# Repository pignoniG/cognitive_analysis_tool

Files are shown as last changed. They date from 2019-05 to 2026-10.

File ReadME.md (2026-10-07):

# Cognitive Workload Tool 2.0

Luminance-compensated pupillometry: an estimate of cognitive workload from the pupil that can be used outside the
laboratory's constant lighting.

The pupil dilates with cognitive workload but reacts far more strongly to light. The tool estimates the pupil size
the light reaching the eye should produce (Watson & Yellott's unified formula, with the participant's latency and
pupil dynamics), and reports what is left, the **ΔPD**:

```
ΔPD(t) = measured pupil(t) − expected pupil(luminance(t))
```

The luminance is estimated from the eye tracker's scene video and gaze: a circle around the gaze point weighted
against the rest of the view. On a headset it comes from the display's photometry; with glasses trackers, the
absolute level comes from a lux sensor worn on the tracker.

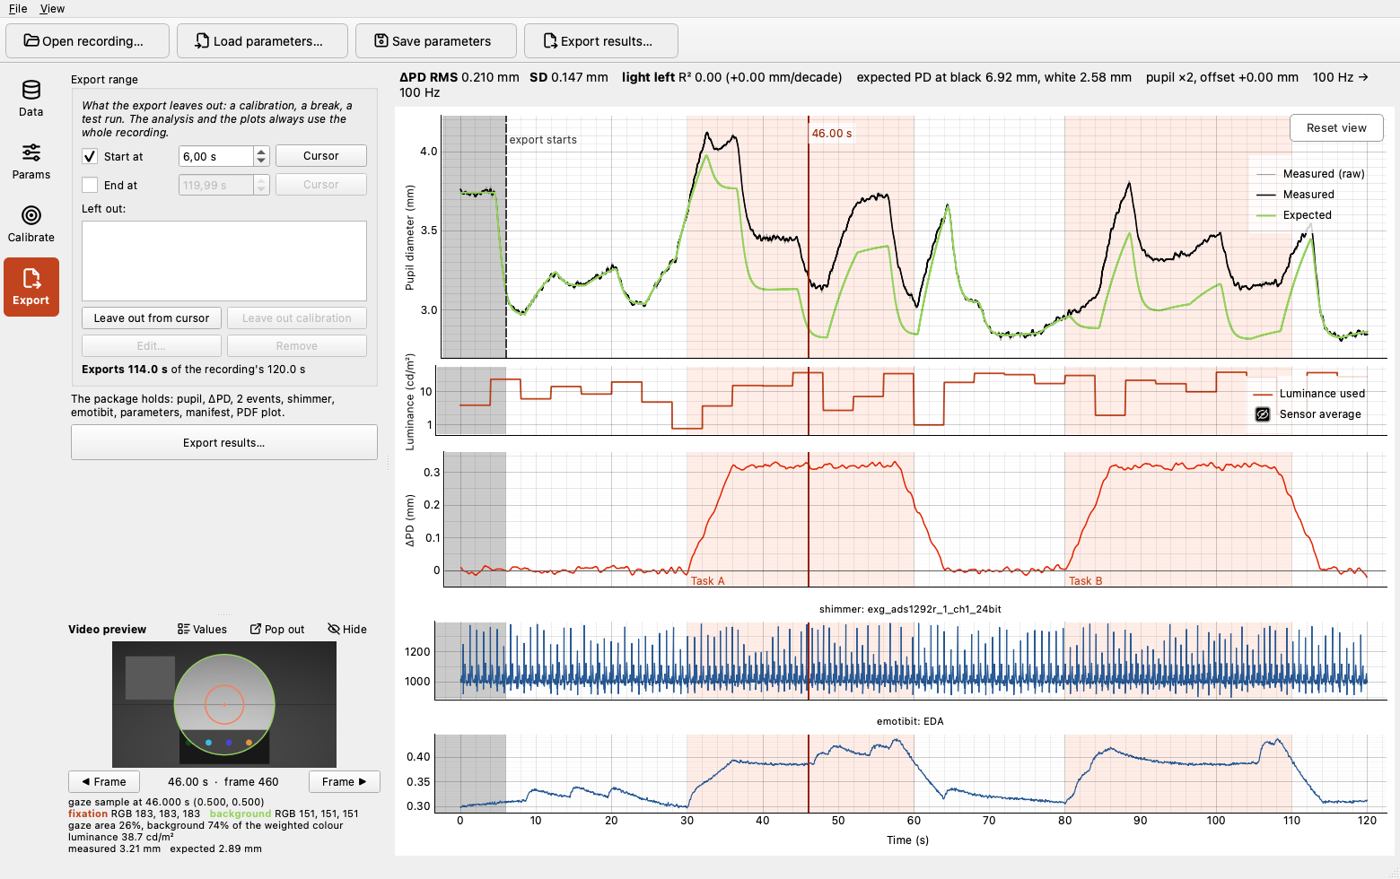
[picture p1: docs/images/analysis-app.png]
The analysis app on a synthetic recording: measured and expected pupil, luminance, ΔPD with two task phases, and the ECG and EDA from the sensor logger


*The analysis app on synthetic data: a task that dilates the pupil twice, the light that changes every few seconds, and the ΔPD that is left once the light is accounted for, with the Shimmer's ECG and the EmotiBit's EDA on the same time axis.*

**Documentation:** https://pignonig.github.io/cognitive_analysis_tool/ covers installation, usage, the device
formats and every processing step ([Processing at a glance](https://pignonig.github.io/cognitive_analysis_tool/processing/pipeline/)).
Its source is in `docs/`.

> Version 2.0 is in development. The 1.x tools are kept, for archive only, on the `legacy-*` branches.

## Supported devices

| Device | Recording | Luminance from | Support |
|---|---|---|---|
| Varjo XR-4 | Varjo Base eye tracking recorder | the display: scene capture, display photometry, participant light sensitivity | tested |
| Pupil Core | Pupil Player export | external lux sensor + scene video | tested |
| Pupil Neon | Pupil Cloud Timeseries export or native format | external lux sensor + scene video | experimental |
| Tobii Pro Glasses 3 | recording folder from the SD card | external lux sensor + scene video | experimental |

Experimental readers were written from the manufacturer's documentation and have not yet been checked on a real
recording; every result from them carries a warning.

## The tools

**Analysis app** (`cwtool-gui`). Open a recording folder: the scene video is analysed in the background (or loaded
from its cache), and every parameter change updates the measured and expected pupil and ΔPD plots at once. A video
preview shows the analysed areas on the scene frame at the cursor. Sensor files from the logger can be shown under
ΔPD. **Export** writes one package for the participant: pupil, ΔPD, per-event means, lux and sensor files, the
parameters used and a manifest, all cut to an *export range* that leaves out a calibration, a break or a test run.

**Sensor logger** (`cwtool-logger`). Records the lux sensor, a Shimmer (ECG and more) and an EmotiBit side by side
on the computer's clock, with the phases of the experiment, one folder per recording. Live plots let you check
the signals before recording.

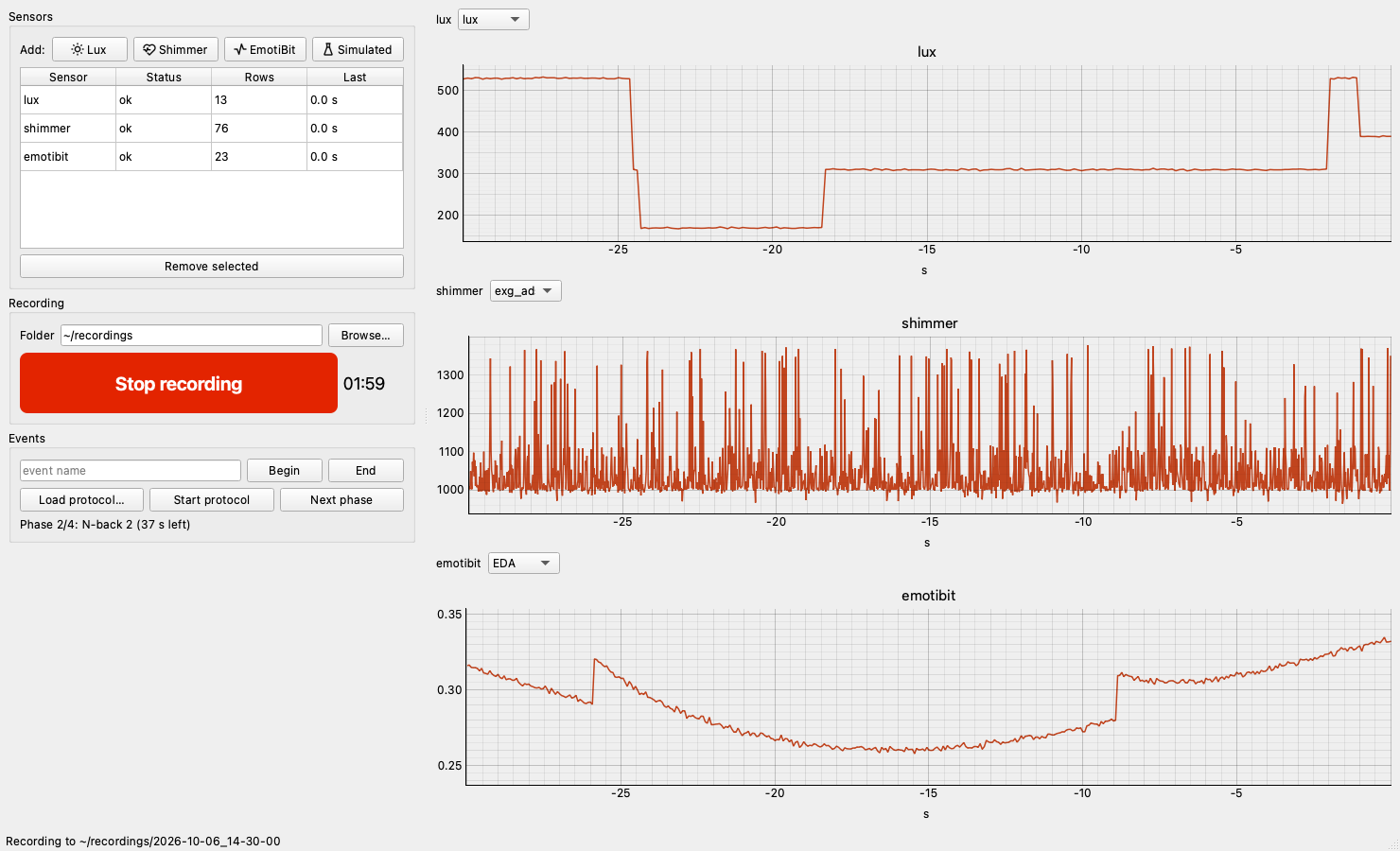
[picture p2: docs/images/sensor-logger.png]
The sensor logger recording a lux sensor, a Shimmer and an EmotiBit, with a protocol running


**Calibration presenter** (a web page, no install). Plays the participant calibration sequence full-screen on a
display or inside a VR headset, and logs every run.
[Open it](https://pignonig.github.io/cognitive_analysis_tool/calibration-tool/index.html) or open
`docs/calibration-tool/index.html` from a local web server.

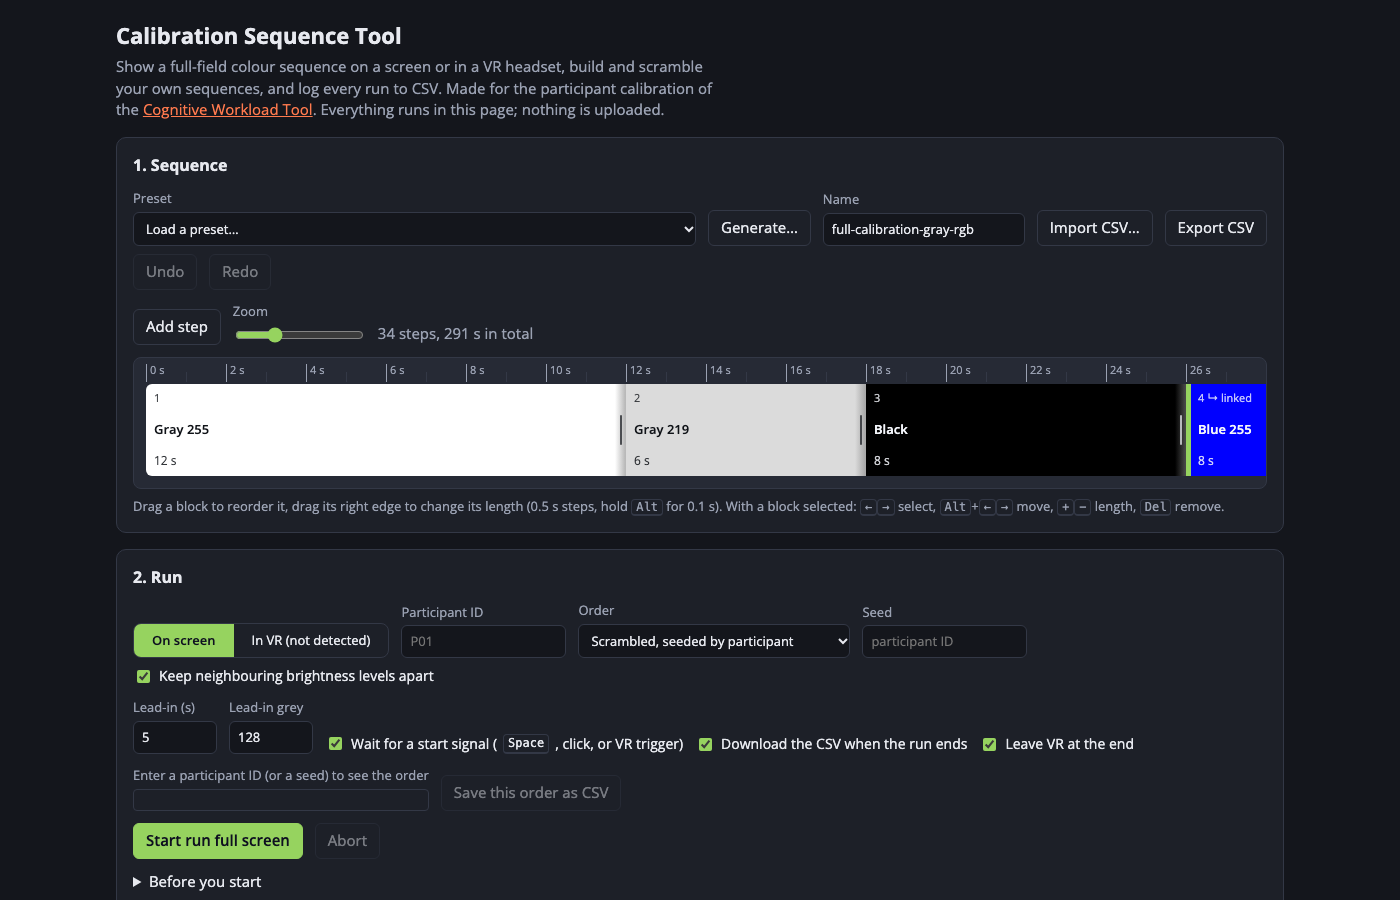
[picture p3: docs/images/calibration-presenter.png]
The calibration presenter: the sequence editor and the run settings


*All screenshots use synthetic data.*

## Install and run

Python 3.10 or newer, on Windows, macOS or Linux.

```bash
git clone -b master_v2.0 https://github.com/pignoniG/cognitive_analysis_tool.git
cd cognitive_analysis_tool
pip install -e ".[gui,logger]"       # "gui" alone if you do not need the sensor logger

cwtool-gui [path/to/recording]                                   # analysis app
cwtool path/to/recording --params participant.json --plot        # command line, batch processing
cwtool-logger                                                    # sensor logger
```

On macOS, start the sensor logger from Terminal when using a Shimmer (macOS ends programs that use Bluetooth unless the
app that started them may); see the [sensor logger page](https://pignonig.github.io/cognitive_analysis_tool/usage/logger/).

## What is in the repository

| Path | Content |
|---|---|
| `cwtool/` | the analysis as a Python package that runs without a GUI; `cwtool/gui/` is the Qt app, `cwtool/logger/` the multi-sensor logger (lux, Shimmer, EmotiBit) |
| `tools/` | the command-line lux sensor logger and an experiment event logger |
| `docs/` | the documentation site, including the calibration presenter (a web page that plays the calibration sequence on a screen or in VR) and the screenshots in `docs/images/` |
| `Lux Sensor/` | firmware for the lux logger and the 3D-printable mount for the Pupil Core |
| `tests/` | pytest suite with synthetic recordings for every device |

## Participant calibration (Varjo)

A short full-field colour sequence, shown in the headset with the calibration presenter, gives each participant's
light sensitivity and channel weights, then their response latency and pupil dynamics (the pupil scale and offset stay
values you set). These are saved with the participant's parameters and applied to their other recordings. The display's
own photometry (black and white luminance, gamma) is kept in a separate file. For glasses with a lux sensor the same
sequence, shown on a screen, fits the light sensitivity and the pupil offset. See
[Participant calibration](https://pignonig.github.io/cognitive_analysis_tool/usage/calibration/).

## Development

```bash
pip install -e ".[gui,dev]"
pytest
pip install -r docs/requirements.txt && mkdocs serve   # documentation preview
```

Known problems and decisions still open are tracked in `docs/OPEN_ISSUES.md`.

## Publications

- Pignoni G., Komandur S., Volden F. (2021). *Accounting for Effects of Variation in Luminance in Pupillometry for
  Field Measurements of Cognitive Workload*. IEEE Sensors Journal. The lux sensor method.
- Pignoni G., Grandi F., Peruzzini M. *Toward Reliable Pupillometry in Extended Reality Environments*. Manuscript in preparation, not yet published. The
  Varjo method.

Earlier and related publications (2019–2022) are listed in the documentation's
[References](https://pignonig.github.io/cognitive_analysis_tool/reference/references/). The tool started as part of a
master's thesis in MIXD at NTNU Gjøvik (2018–2019).

## License

MIT License, see [LICENSE.md](LICENSE.md). The icons are [Tabler Icons](https://tabler.io/icons) (MIT,
`cwtool/gui/icons/LICENSE-tabler-icons.txt`).

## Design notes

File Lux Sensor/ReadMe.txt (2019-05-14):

This folder contains the Arduino code for the sensor logger modules:
It has been tested in two configurations: 

Adalogger FeatherWing + Adafruit Feather M4 Express + Adafruit TSL2591 High Dynamic Range Digital Light Sensor

https://www.adafruit.com/product/3857

https://www.adafruit.com/product/1980

Or

Arduino Nano + Nano Data Logging Shield Deek-Robot ID 8105 + Adafruit TSL2591 High Dynamic Range Digital Light Sensor

https://forum.arduino.cc/index.php?topic=528237.0
https://www.adafruit.com/product/1980

They are equivalent in functionality but since the modules have different RTC the code is different.

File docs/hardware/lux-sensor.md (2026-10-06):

# Lux sensor hardware

Glasses-type trackers (Pupil Core, Pupil Neon, Tobii Pro Glasses 3) see the world through a scene camera with automatic exposure, so
their video cannot tell how bright the scene is. An [Adafruit TSL2591](https://www.adafruit.com/product/1980) light
sensor mounted on the tracker, facing forward, measures the illuminance at the eye; the analysis turns it into the
average luminance of the view (see [Luminance](../processing/luminance.md#lux-sensor-devices)).

The firmware and 3D-printable mount are in the repository's `Lux Sensor/` folder.

## Two ways to log

| | Logged to a computer | Logged to the SD card |
|---|---|---|
| Hardware | microcontroller + sensor | microcontroller + data logging shield (RTC, SD card) + battery + sensor |
| Recording | the [sensor logger](../usage/logger.md) (or `tools/lux_logger.py`) over USB | power the board on |
| Clock | the computer's, the same as the eye tracker's | the board's real-time clock: drifts seconds per day, no time zones |
| Cable | 3–4 m ribbon cable to the computer | 1.5 m, logger carried by the participant |

Either way the readings (about 10 per second) are logged with the time of each. The sensor logger writes one `lux.csv`
per recording (`unix time (s)`, `lux`, with a header). The SD card logger and `tools/lux_logger.py` write one CSV per
hour, `<month>_<day>_<hour>.csv`, with the Unix time in milliseconds in the first column and lux in the fifth. The
analysis reads both.

With the SD card logger, set the real-time clock to local time and correct the remaining offset with the
**time lag** parameter (for example, 3600 s for a clock one hour off).

## Bill of materials

Tested configurations (the two differ only in their real-time clock, so each has its own firmware):

**Adafruit Feather** (`Lux Sensor/Adalogger FeatherWing/Light_sd_log_direct`)

- [Adafruit Feather M4 Express](https://www.adafruit.com/product/3857), with a built-in battery charger
- [Adalogger FeatherWing](https://www.adafruit.com/product/2922): real-time clock (PCF8523) and SD card
- [3.7 V lithium battery](https://www.adafruit.com/product/1578), [CR1220](https://www.adafruit.com/product/380)
  backup battery for the clock, a 4–8 GB micro SD card
- Adafruit TSL2591 sensor and a four-conductor ribbon cable

**Arduino Nano** (`Lux Sensor/Arduino Nano/Light_sd_log_direct_nano`)

- Arduino Nano and the Deek-Robot 8105 Nano data logging shield (DS1307 real-time clock)
- Adafruit TSL2591 sensor and a four-conductor ribbon cable

Only the microcontroller and sensor are needed when always logging to a computer.

## Wiring

| TSL2591 | Microcontroller |
|---|---|
| Vin (3–5 V) | 3V |
| GND | GND |
| SCL | SCL (I²C clock) |
| SDA | SDA (I²C data) |

## Firmware

Flash the board with the Arduino IDE. The sketches need the `Adafruit_Sensor` and `Adafruit_TSL2591` libraries, and
the RTC library for the board's clock (`RTC_PCF8523` from RTClib for the FeatherWing, `DS1307RTC` for the Nano
shield). Set the clock once with the RTC library's example sketch.

Adafruit's guides: [Feather M4 setup](https://learn.adafruit.com/adafruit-feather-m4-express-atsamd51/setup),
[Adalogger RTC](https://learn.adafruit.com/adafruit-adalogger-featherwing/adafruit2-rtc-with-arduino),
[TSL2591 wiring and test](https://learn.adafruit.com/adafruit-tsl2591/wiring-and-test).

## Mount

`Lux Sensor/Mount Hardware/Adafruit Pupil lumiance sensor kit.stl` holds the sensor on the Pupil Core's world
camera and includes cable clips. It prints on a generic filament printer.

## Calibration

The analysis converts lux to average luminance with

\[
\bar L = \frac{g \cdot E + o}{\Omega}
\]

where \(E\) is the reading in lux, \(g\) and \(o\) an optional recalibration of it (default 1 and 0: the chip's own
lux), and \(\Omega\) = 2.2 the ratio of illuminance to average luminance for the sensor in its housing (parameters
`lux_gain`, `lux_offset`, `lux_solid_angle`). 1.x used \(g\) = 1.706061 and \(o\) = 0.66935; see below for why 2.0
does not.

**Where 2.2 comes from.** It is not a solid angle, although 1.x called it one: for a uniform field of luminance
\(L\), a sensor with angular response \(R(\alpha)\) reads

\[
E = L \int_0^{2\pi}\!\!\int_0^{\theta} R(\alpha)\,\sin\alpha\;d\alpha\,d\varphi
\]

over the field it sees. The TSL2591's response is close to a cosine (datasheet, Fig. 12; over a hemisphere the
integral is 3.10, against \(\pi\) for an ideal cosine). In the printed housing the board sits at the bottom of the
funnel, so the photodiode is level with the funnel's base, 3.7 mm below its rim (10.6 mm across); the rim limits
the field to a half-angle of 55°. The integral over that field is 2.12–2.15 (depending on where the chip sits
under the funnel), within 2–4 % of 2.2, i.e. about 0.01 mm of modelled pupil.

**Where the 1.x gain and offset came from.** The 1.x values \(g\) = 1.706061, \(o\) = 0.66935 came from a comparison in the 2019 master thesis (Pignoni, "Quantitative evaluation tool of cognitive workload",
NTNU; section 4.2, Table 2 and Figure 13): a projected screen in a dark room was measured by a Konica Minolta CS-2000
spectroradiometer (a 2° spot at its centre, its brightest part) and by the head-mounted sensor (lux / 2.2, a field of
more than 60° including the darker surround). Regressing the spectroradiometer on the sensor gives a slope of 1.709
and an intercept of 0.54 cd/m² (r = 0.9998, on the rounded table). The line therefore maps the sensor's field average
onto the luminance of the centre of that particular scene; it corrects a field-of-view mismatch, not the sensor. In
other scenes the factor differs (about 1 in a uniform field), and with the scene video it would correct twice: the
video already turns the field average into the luminance at the gaze. 2.0 therefore uses the chip's lux as reported
(about ±15 % between units, datasheet) ([open issue 23](../OPEN_ISSUES.md)).

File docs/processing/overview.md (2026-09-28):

# Pipeline overview

```mermaid
flowchart TD
    REC[Recording<br/>pupil, gaze, scene video, lux] --> VID[Scene video analysis<br/>gaze circle + background, per gaze sample]
    VID --> CACHE[(cwtool_video.csv<br/>cache)]
    CACHE --> LUM[Luminance<br/>display photometry or lux sensor]
    REC --> PUP[Pupil signal<br/>scale, range, artefacts, eyes, resample, smooth]
    LUM --> MOD[Expected pupil<br/>Watson & Yellott + delay + dynamics]
    PUP --> ALN[Scale and alignment]
    MOD --> ALN
    ALN --> DPD[ΔPD<br/>windowed measured − expected]
    DPD --> OUT[Plots, CSV export, per-event means]
    MOD -.-> FIT[Calibration fit<br/>light sensitivity, channel weights,<br/>latency, dynamics, scale, offset]
    PUP -.-> FIT
```

The analysis runs in two passes with very different costs:

1. **Video pass** (`cwtool/video.py`), seconds to minutes: decodes the scene video and measures, for every valid gaze
   sample, the colour inside a circle around the gaze point and over the background. Colours are stored for a grid
   of gamma values, so nothing in the second pass needs the video again. The result is cached next to the
   recording.
2. **Signal pass** (`cwtool/pipeline.py`), a fraction of a second: everything else. It re-runs on every parameter
   change, which is what makes the app's plots live.

## Steps and where to read about them

Every step with its parameters, defaults and functions is listed in order on one page:
[Processing at a glance](pipeline.md).

| Step | Module | Page |
|---|---|---|
| Read the device's files into a `Recording` | `devices/` | [Devices](../devices/index.md) |
| Measure gaze circle and background colours | `video.py` | [Scene video analysis](video.md) |
| Turn colours into cd/m² | `luminance.py`, `lux.py`, `pipeline.prepare` | [Luminance](luminance.md) |
| Clean and resample the pupil | `pipeline.prepare` | [Pupil signal](pupil-signal.md) |
| Expected pupil for that luminance | `model.py`, `pipeline.expected_pupil` | [Expected pupil model](model.md) |
| Offset, ΔPD, statistics, events | `pipeline.run` | [ΔPD and alignment](delta-pd.md) |
| Participant parameters from the calibration sequence | `calibration.py`, `photometry.py`, `fit.py` | [Calibration fit](calibration-fit.md) |

## Clocks

Everything runs on the recording's relative clock: seconds from the first scene video frame. Lux readings are moved
onto it with `epoch_start`, and the **time lag** parameter shifts the luminance signal (video and lux) to correct a
known offset. Exports carry both the relative and the Unix time.

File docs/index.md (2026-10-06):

# Cognitive Workload Tool

The pupil dilates with cognitive workload, but it reacts far more strongly to light. This tool estimates how
large the pupil *should* be for the light reaching the eye, and reports what is left: the **ΔPD**
(pupil diameter difference), a measure of cognitive workload that can be used outside the laboratory's constant
lighting.

\[
\Delta PD(t) = PD_\text{measured}(t) - PD_\text{expected}\big(L(t)\big)
\]

The expected pupil comes from the Watson & Yellott unified formula, driven by an estimate of the luminance \(L\)
the participant is looking at. That estimate is built from the eye tracker's scene video and gaze: a small circle
around the gaze point weighted against the rest of the view. With glasses-type trackers the absolute level comes
from an external lux sensor worn on the tracker.

## Supported devices

| Device | Recording | Pupil | Luminance from |
|---|---|---|---|
| [Varjo XR-4](devices/varjo.md) | Varjo Base eye tracking recorder | mm (radius ×2 in older exports, diameter in newer ones) | the headset's display, via the scene capture, the display photometry and the participant's fitted light sensitivity |
| [Pupil Core](devices/pupil-core.md) | Pupil Player export | mm (3D model) or px | external lux sensor, distributed with the scene video |
| [Pupil Neon](devices/pupil-neon.md) (experimental) | Pupil Cloud Timeseries export or native format | mm | external lux sensor, distributed with the scene video |
| [Tobii Pro Glasses 3](devices/tobii-g3.md) (experimental) | recording folder from the SD card | mm | external lux sensor, distributed with the scene video |

One recording is analysed at a time. A new device needs only a reader module; the analysis is shared
(see [Devices](devices/index.md)).

## What is in the package

- `cwtool`: the analysis, as a Python package that runs without a GUI.
- `cwtool-gui`: a Qt desktop app for Windows, macOS and Linux, with live plots, the video preview, the calibration
  sequence overlay and the participant calibration fit.
- `cwtool`: a command-line tool for batch processing.
- `cwtool-logger`: a Qt app that records the lux sensor, a Shimmer and an EmotiBit, with experiment events
  ([Sensor logger](usage/logger.md)).
- `tools/`: the original command-line lux sensor logger and experiment event logger.

## Where to start

- New user: [Installation](getting-started/installation.md), then [First analysis](getting-started/first-analysis.md).
- Varjo study: [Participant calibration](usage/calibration.md).
- Understanding the numbers: [Pipeline overview](processing/overview.md).
- Known problems and decisions still open: [Open issues](OPEN_ISSUES.md).

!!! note "Version 2.0 is in development"
    This documentation describes the `master_v2.0` branch. Version 1.x lives on the legacy branches:
    `legacy-pupilCore` (the macOS application for the Pupil Core), `legacy-varjo` (the Varjo build) and
    `legacy-TobiiProIII` (the Tobii Pro Glasses 3 build).

## Publications

- Pignoni G., Komandur S., Volden F. (2021). *Accounting for Effects of Variation in Luminance in Pupillometry for
  Field Measurements of Cognitive Workload*. IEEE Sensors Journal. The lux sensor method used for the glasses trackers.
- Pignoni G., Grandi F., Peruzzini M. *Toward Reliable Pupillometry in Extended Reality Environments*. Manuscript in preparation, not yet published. The
  Varjo method: display photometric calibration and the two-circle luminance estimate.

Earlier and related publications (2019–2022), the models and related work are listed in
[References](reference/references.md).

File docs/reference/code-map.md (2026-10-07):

# Code map

```text
cwtool/
├── recording.py        Recording, DeviceProfile, Event: the device-independent data model
├── params.py           Parameters (signal pass), VideoSettings (video pass), DisplayPhotometry (its own file);
│                       JSON load/save, 1.x conversion, unused_parameters() for the GUI
├── devices/
│   ├── __init__.py     READERS, detect(), load()
│   ├── common.py       event logs, markers → events, binning, sample rate, field of view (pinhole and lens distortion)
│   ├── varjo.py        Varjo XR-4 (Varjo Base)
│   ├── pupil_core.py   Pupil Core (Pupil Player export)
│   ├── neon.py         Pupil Neon (Pupil Cloud export, native format), experimental
│   └── tobii_g3.py     Tobii Pro Glasses 3 (SD card recording folder), experimental
├── lux.py              lux log files (hourly 1.x files and the logger's lux.csv): find, read, smooth, lux → average luminance
├── sensors.py          the sensor logger's Shimmer and EmotiBit files: find, read, cut, write
├── trim.py             Trim: the part of a recording an export keeps (start, end, left-out segments)
├── video.py            scene video pass: frame clock, decoding (PyAV/OpenCV), parallel chunks, two-area
│                       measurement, gamma grid, gaze weighting (VideoResult.weighted), cache
├── luminance.py        code values → linear, relative and absolute luminance
├── model.py            Watson & Yellott, Stanley & Davies, delay, attack/release, transient
├── pipeline.py         prepare(), run(), export(): from recording + video pass + parameters to ΔPD
├── calibration.py      calibration sequences: built-in, CSV, locate in a recording
├── photometry.py       step 1 of the participant fit: light sensitivity and channel weights from step levels
├── fit.py              step 2: latency (from onsets), dynamics and transient (pupil offset optional)
├── logger/             the multi-sensor logger (no Qt except gui.py); see usage/logger.md
│   ├── base.py         Source (one sensor stream), ClockMapper (device clock → Unix time)
│   ├── session.py      Logger (sources, live buffers, session folder, writer thread), EventLog
│   ├── sinks.py        CsvSink
│   ├── protocol.py     protocol files (name,duration)
│   ├── clockcheck.py   timestamp checks of a recorded session (regularity, Shimmer drift, Shimmer vs EmotiBit offset)
│   ├── gui.py          the window (cwtool-logger), plot scaling, stall watchdog
│   └── sources/        lux (serial), shimmer (pyshimmer), lsl (EmotiBit via the Oscilloscope), simulated;
│                       rfcomm_mac.py + rfcomm_helper.py: direct Bluetooth channel on macOS
├── cli.py              the cwtool command
                        (gui/ and logger/ each have a __main__.py: python -m cwtool.gui, python -m cwtool.logger)
├── plot.py             matplotlib figure for exports
├── palette.py          project colours, shared by the app, its plots and the PDF plot
└── gui/
    ├── main_window.py  window, menus, recording/video/calibration panels, background tasks
    ├── param_panel.py  parameter editors (every Parameters field must have one)
    ├── plots.py        pyqtgraph plots, sequence overlay, cursor, sensor plots, export range overlay
    ├── side_panel.py   the rail of tabs, pills, numbered steps and the preview holder of the left column
    ├── trim_panel.py   the export range editor in the sidebar
    ├── icons.py        the icon loader (Tabler outline SVGs in icons/, drawn in the palette's colours)
    ├── photometry_dialog.py  result window of the light sensitivity fit
    ├── video_preview.py      scene frame at the cursor with the analysis circles
    └── workers.py      QThread wrapper for the video pass and the fit

tools/
├── lux_logger.py       lux sensor over USB serial → hourly CSVs (1.x format; the sensor logger writes lux.csv)
├── event_logger.py     experiment phases → event_log CSV
└── example_protocol.csv

tests/                  pytest suite with synthetic recordings for every device (conftest.py); one file per area,
                        each with a header saying what it covers
docs/                   this site (MkDocs)
Lux Sensor/             lux logger firmware and 3D-printable mount
```

## Main entry points

| Function | Does |
|---|---|
| `devices.load(folder, device=None, **options)` | read a recording |
| `video.analyse_video(video, time, gaze, settings, frame_times=...)` | video pass |
| `video.VideoResult.load_cached(...)` / `.save(...)` | cache |
| `pipeline.run(rec, video, params)` | signal pass, returns a `Result` |
| `pipeline.export(result, rec, params, folder, trim=, sensors=)` | the export package: CSVs, sensor files, parameters, manifest; trimmed |
| `sensors.load_sensors(folder, epoch_start, duration)` | the logger's sensor files, cut to a recording |
| `calibration.locate(time, rgb, sequence, gamma)` | find the calibration sequence |
| `photometry.fit_light_response(rec, video, params, start, sequence)` | participant fit, step 1: light response |
| `fit.fit_calibration(rec, video, params, start, end, sequence=...)` | participant fit, step 2: latency and dynamics |
| `pipeline.calibrate_camera(rec, video, params)` | full-scale luminance of a fixed-exposure scene camera |
| `logger.Logger().add(source)` / `.start_recording(folder)` / `.stop_recording()` | record sensors into a session folder |

The processing steps and the functions that carry them out are listed in order in
[Processing at a glance](../processing/pipeline.md).

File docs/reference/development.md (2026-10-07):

# Development

## Setup

```bash
pip install -e ".[gui,plot,logger,dev]"
pytest
```

The logger's tests (`tests/test_logger.py`) use simulated sensors, a fake lux board and a slow disk, so they need no
hardware and no Bluetooth; the Shimmer and EmotiBit paths were checked by hand on real devices. To run the logger's
window headless, set `QT_QPA_PLATFORM=offscreen`.

The tests build synthetic recordings for every device (`tests/conftest.py`: `write_varjo_recording`,
`write_core_recording`, `write_neon_recording`, `write_tobii_g3_recording`) with known pupil, gaze and scene colours, so they run without real
data. The GUI tests need a display or `QT_QPA_PLATFORM=offscreen`.

## Conventions

- The analysis (`cwtool/`, except `gui/` and `logger/gui.py`) does not import Qt, so it runs headless and in scripts.
- Qt code imports PySide6 before pyqtgraph (`logger/gui.py` also sets `PYQTGRAPH_QT_LIB`): with PyQt6 also installed,
  pyqtgraph would load it and two Qt copies in one process crash.
- Hardware calls that can block (device discovery, connecting) run in a background task, never in the window's
  thread; disk writes of the logger run in their own thread.
- Readers return NaN for invalid samples; the pipeline never sees device-specific validity flags.
- Parameters that do not change the video pass belong in `Parameters`; those that do belong in `VideoSettings` (and
  are part of the cache key).
- Every `Parameters` field needs an editor in `gui/param_panel.py`; a check at start-up enforces it.
- Changing what the video pass stores means bumping `CACHE_FORMAT` in `video.py`.
- Inconsistencies found in the code, the data or the papers go in `docs/OPEN_ISSUES.md`.

### Comments

- **Every source file starts with a header** saying what it contains: the module docstring of a Python file (tests
  included), a `//` comment at the top of an Arduino sketch, a comment in the page for the calibration presenter, the
  settings and the workflow. Keep it to what the file is for and what it does not do, not a list of its functions.
- **Every public class and function has a docstring** (one line is enough when the name and the arguments say the
  rest): what it returns and the units (s, mm, cd/m²) and the clock a time is on, where that is not obvious. Private
  helpers get one when their logic is not clear from the code.
- **Comments explain why**, not what: the assumption behind a number, the reason for an order of operations, the open
  issue a workaround refers to (`issue 47`). Tests are named after what they check and need no docstring.
- A docstring that disagrees with the code is a bug: change both together.

## Icons

The windows use Tabler's outline icons (MIT; the licence is in `cwtool/gui/icons/`), stored as SVG files and drawn
by `cwtool.gui.icons.icon(name, size)` in the colours of the current palette, at twice the resolution on high-DPI
screens. To add one, copy its SVG from [tabler.io/icons](https://tabler.io/icons) (outline) into `cwtool/gui/icons/`,
add its name to `NAMES` in `icons.py` and use `icon("name")`; a test checks that every named icon has a clean file
and that no file is left unnamed. The SVGs are included in the installed package (`package-data` in `pyproject.toml`).

## Documentation

This site is built with [MkDocs](https://www.mkdocs.org/) and the Material theme from `docs/` and `mkdocs.yml`.

```bash
pip install -r docs/requirements.txt
mkdocs serve          # live preview at http://127.0.0.1:8000
mkdocs build --strict # what the deployment runs
```

Pushes to `master_v2.0` that touch the docs publish the site to GitHub Pages through `.github/workflows/docs.yml`
(repository **Settings → Pages → Source: GitHub Actions**).

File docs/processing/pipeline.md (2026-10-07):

# Processing at a glance

Every step from a recording folder to the exported ΔPD, in the order the code runs it. For each step: what it does,
the parameters and defaults that control it, and the function that does it. The linked pages give the reasoning and
the equations. The defaults are those of `Parameters()` and `VideoSettings()` in `cwtool/params.py`; all parameters
are listed in [Parameters](../reference/parameters.md).

```mermaid
flowchart LR
    A[1 Read] --> B[2 Video pass]
    B --> C[3 Luminance]
    A --> D[4 Pupil signal]
    C --> E[5 Expected pupil]
    D --> F[6 Scale and offset]
    E --> F
    F --> G[7 ΔPD]
    G --> H[8 Statistics, events, export]
    B -.-> K[9 Calibration fit]
    D -.-> K
    E -.-> K
```

Steps 1 and 2 run once per recording (the video pass is cached). Steps 3–8 are the **signal pass**, `pipeline.run`,
which re-runs on every parameter change. Step 9 runs on demand and writes its results into the parameters.

## 1. Read the recording

`devices.load(folder, device=None, **options)` → `Recording` ([Devices](../devices/index.md))

| | |
|---|---|
| Detection | each reader's `detect(folder)` in turn: Varjo, Pupil Core, Pupil Neon, Tobii Pro Glasses 3 |
| Pupil | per eye, in device units; NaN where invalid |
| Validity | Varjo: tracking status 1 or lower (overall or either eye); Core: confidence below 0.6; Neon: not worn, and 0.1 s around Cloud blinks; Glasses 3: empty samples. Zero or negative diameters are invalid on every device |
| Grid | irregular samples are averaged into bins at the measured rate (`common.bin_samples`, `common.sample_rate`) |
| Time base | seconds from the first scene video frame (can start below 0); `epoch_start` is its Unix time |
| Gaze | normalised scene video coordinates, origin top left |
| Lux | the lux logs in the recording, its `lux` subfolder or `--lux`/**Choose lux folder** (`lux.find_lux_folder`, `lux.read_lux`), moved onto the recording clock with `epoch_start` |
| Events | `event_log` CSV (`common.read_event_log`) plus Neon and Glasses 3 recording events (`common.events_from_markers`) |
| Profile | pupil unit and scale, luminance source (`display` or `lux_sensor`), camera field of view, circular scene, native rate, adapting field, `experimental` |

Neon and Glasses 3 readers are **experimental**: every result from them carries a warning (step 8).

## 2. Scene video pass

`video.analyse_video(...)` → `VideoResult`, cached as `cwtool_video.csv` + `.json` ([Scene video analysis](video.md))

| Step | Settings | Code |
|---|---|---|
| Match each valid gaze sample to its frame: nearest recorded timestamp (Core, Neon) or constant frame rate (Varjo, Glasses 3) | – | `FrameClock` |
| Decode (PyAV, else OpenCV) in parallel chunks of at least 150 frames; only frames with gaze are converted | `--workers` (default one per core) | `_frames_pyav`, `_frames_opencv` |
| Downscale with nearest-neighbour sampling, convert to RGB | `analysis_width` 500 px | `prepare_frame` |
| Gaze circle: disc of the given radius at the gaze point | `fixation_radius_deg` 16.35° (radius = degrees / vertical field of view × height) | `radii`, `analyse_frame` |
| Background: whole frame, or a centred circle on circular (Varjo) videos; minus the gaze circle | `field_radius` 0.8, `background_excludes_fixation` on | `field_mask` |
| Per area and channel: 256-bin histogram → mean code value and mean of \((C/255)^\gamma\) for γ = 1.4, 1.6 … 3.0 (gaze circle, background, whole visible scene) | – | `_histograms`, `_means` |
| Cache, reused only if format, γ grid, settings, video name, frame clock and gaze all match | – | `VideoResult.save`, `load_cached` |

## 3. Luminance \(L(t)\), cd/m²

`pipeline.prepare` ([Luminance](luminance.md))

**3a. Linear colour at the current gamma.** The stored linear means are interpolated to `gamma` (default 2.2) in log
space (`video.at_gamma`), and the two areas weighted: \(\mathbf{C}_w = w\,\mathbf{C}_\text{gaze} + (1-w)\,\mathbf{C}_\text{background}\),
`fixation_weight` \(w\) = 0.26 (`VideoResult.weighted`).

**3b. One of four methods**, chosen from the device and the data (reported as `Result.luminance_mode`):

| Mode | When | Luminance | Parameters | Code |
|---|---|---|---|---|
| display | display devices (Varjo) | \(\sum_c k_c\,(L_\text{max}\,\tfrac{g_c}{\bar g}\,C_{w,c} + L_\text{min}(1-C_{w,c}))\), \(k\) = BT.709 weights | `l_min` 0.01, `l_max` 100 cd/m², `gamma` 2.2 (display photometry file); `gain_r/g/b` 1 (participant) | `scene_luminance`, `luminance.absolute_luminance` |
| lux sensor | glasses with a lux log | \(\bar L \cdot Y_w / Y_\text{frame}\), the ratio kept between 1/limit and limit, \(\bar L = (g\,E + o)/\Omega\) from the smoothed lux \(E\) (Savitzky–Golay 11, order 6) | `lux_gain` 1, `lux_offset` 0, `lux_solid_angle` 2.2, `lux_use_video` on (off: \(\bar L\) alone), `lux_ratio_limit` 10 | `luminance_from_lux`, `relative_luminances`, `lux.smooth`, `lux.average_luminance` |
| camera, fixed exposure | glasses without a lux log, `camera_exposure` = fixed | \(L_\text{white}\,\tfrac{t_\text{ref}}{t}\,Y_w\); warning if the gaze area is saturated in more than 5 % of samples | `camera_white` 1000 cd/m², `camera_reference_ms` 0, `camera_exposure_ms` 0 | `relative_luminances`, `Parameters.camera_full_scale`, `clipped_fraction` |
| camera, relative | glasses without a lux log, `camera_exposure` = auto | as display, with a warning that it is only relative | `l_min`, `l_max`, `gamma` | `scene_luminance` |

\(Y\) is the relative luminance with the BT.709 weights and the channel balance \(g_c/\bar g\).

**3c. Time.** Video and lux luminance are interpolated onto the analysis grid (step 4), with their timestamps shifted
by `timelag` (0 s).

**3d. Coverage.** Where the luminance is only interpolated or held, it is unknown, and those samples are marked
invalid like long pupil gaps (left out of ΔPD, the offset and the statistics): outside the lux log or between lux
readings more than 1 s apart (`LUX_MAX_GAP`), and, whenever the video enters the luminance, between analysed video
samples more than `max_gap` apart (gaze lost or outside the scene video). A note gives the share when it exceeds 1 %.
The expected pupil is still computed through such stretches, so its filters run on.

## 4. Pupil signal

`pipeline.prepare` ([Pupil signal](pupil-signal.md))

| # | Step | Parameters | Code |
|---|---|---|---|
| 4.1 | Scale to mm: device units × profile `pupil_scale` × `pupil_correction`. Pixel data have no scale yet (step 6) | `pupil_correction` 1 | `prepare` |
| 4.2 | Range: diameters outside 1–9 mm removed, per eye (skipped for pixel data) | `PUPIL_RANGE_MM` | `prepare` |
| 4.3 | Artefacts: speed above the limit towards a sample at least 40 ms away, widened by the padding, per eye (skipped for pixel data) | `max_pupil_speed` 10 mm/s (0 = off), `artefact_padding` 0.05 s | `artefacts` |
| 4.4 | Combine the eyes; `both` averages, bridging a missing eye with the other plus their median difference | `eye` both | `combine_eyes` |
| 4.5 | Resample onto a uniform grid by linear interpolation; gaps longer than `max_gap` marked invalid | `analysis_rate` 100 Hz (0 = native), `max_gap` 0.5 s | `resample` |
| 4.6 | Smooth: Savitzky–Golay order 2 over about 0.5 s (**measured**) and order 6 over about 0.25 s, at least 9 samples (**measured raw**, used by the calibration fits); both NaN in long gaps | – | `prepare` |

## 5. Expected pupil

`pipeline.expected_pupil` ([Expected pupil model](model.md))

| # | Step | Parameters | Code |
|---|---|---|---|
| 5.1 | Light sensitivity: \(s \cdot L\) | `sensitivity` 1 | `steady_pupil` |
| 5.2 | Watson & Yellott: flux = \(sL\) × adapting field area (profile, deg²) × 1 (two eyes) or 0.1 (one); Stanley & Davies diameter; age correction against 28.58 years | `age` 25, `eyes` 2 | `model.watson_yellott` |
| 5.3 | Latency: shift right, padding with the first value; a delay between samples is interpolated linearly | `delay` 0.5 s | `model.delay` |
| 5.4 | Dynamics switch: 5.5–5.6 only when on | `dynamics` on | `dynamic_pupil` |
| 5.5 | Attack/release filter: one pole, τ = `attack` while the expected diameter rises, `release` while it falls; with 2 stages a second `release` stage acts during constriction only (S-shaped onset) | `attack` 6 s, `release` 0.5 s, `constriction_stages` 2 | `model.attack_release` |
| 5.6 | Transient (pupillary escape): minus `transient` × \(h/(h+0.2)\), \(h\) = rise of log₁₀ L over its low-pass with τ = `escape`; delayed and passed through one low-pass (τ = `release`) per constriction stage | `transient` 0 mm (off), `escape` 2 s | `model.escape_transient`, `model.lowpass` |

## 6. Pupil scale and offset

`pipeline.run`, `pipeline.alignment_offset` ([ΔPD and alignment](delta-pd.md))

| Step | Parameters |
|---|---|
| Pixel data: scale so that mean measured = mean expected, then × `pupil_correction` | `pupil_correction` 1 |
| Offset added to the measured pupil: `recording` median(expected − measured) over valid samples; `baseline` the same over the named events (whole recording, with a warning, if none); `fixed` `pupil_offset`; `none` 0 | `alignment` recording, `baseline_events` "Riposo, Rest, Baseline", `pupil_offset` 0 mm |
| Plausibility: warning if the median measured pupil, after the offset, is outside 2–8 mm | – |

## 7. ΔPD

`pipeline.run`, `pipeline.windowed_difference`

1. Measured − expected, averaged over consecutive windows of `cw_window` (0.2 s), ignoring invalid samples; windows
   without any stay NaN.
2. Smoothed with a Savitzky–Golay filter of order 1 over `cw_smoothing` (1) windows on each side; gaps stay NaN.

## 8. Statistics, events, export

| Output | Definition | Code |
|---|---|---|
| ΔPD RMS | root mean square of ΔPD about zero | `residual_rms` |
| ΔPD SD | standard deviation of ΔPD; ΔPD / SD is exported as the normalised ΔPD | `run` |
| Gap fraction | share of the grid left out: pupil gaps longer than `max_gap` and unknown luminance (3d) | `run` |
| Light left in ΔPD | slope of ΔPD on log₁₀ luminance (mm per tenfold luminance) and R² of ΔPD on log₁₀ luminance and its recent change (its excess over a 2 s low-pass), per ΔPD window, leaving out the windows within 0.5 s of a luminance step (a change of more than 0.1 in log₁₀ luminance within 0.1 s); a note above R² 0.1. Near 0 when the model removes the light; NaN when the luminance barely varies or too few windows are left | `light_leakage` |
| Black and white point | expected pupil at `l_min` and `l_max` (display and relative camera modes only) | `run` |
| Warnings | experimental reader, missing lux data, saturation, baseline events not found, implausible pupil | `prepare`, `run` |
| Event means | mean ΔPD (mm and SD units) inside each event | `event_means` |
| Files | `<name>_pupil.csv`, `<name>_cw.csv`, `<name>_events.csv`, `<name>_params.json` (+ `<name>_plot.pdf`) | `export`, `plot.plot_result` |

See [Output files](../reference/outputs.md) for the columns.

## 9. Participant calibration (Varjo)

Run on the participant's calibration sequence, in this order ([Calibration fit](calibration-fit.md),
[Participant calibration](../usage/calibration.md)). The display photometry is taken as given throughout.

| # | Step | Details | Code |
|---|---|---|---|
| 9.1 | Locate the sequence | change points (> 8 code values, ≥ 0.3 s apart) in the gaze circle colour; candidate starts scored by the relative RMS colour error in linear light with one gain per channel, skipping 0.5 s after each change; step length rescaled if the recording's steps differ; at least half of the window must have analysed video. The app rejects matches with an error above 35 % | `calibration.locate` |
| 9.2 | Light response | level per step = mean of the measured raw pupil over its last 30 % (after `delay` + 0.1 s), colour = mean weighted linear colour after 0.5 s; weighted least squares of measured ≈ WY(s · L(gains, γ, Lmin)) (+ d) over log s, log gains (optionally γ, log Lmin with Lmax held, and d), weak priors on gains (SD 1.5 in log) and γ (0.2), none on s; five starting sensitivities; the pupil scale is not fitted. Sets `sensitivity`, `gain_r/g/b` (mean 1), with the options `gamma`, `l_min`, `pupil_offset` −d | `photometry.fit_light_response` |
| 9.3 | Latency | median constriction onset at brightening steps (20–50 % line back to the pre-change level; constrictions ≥ 0.3 mm; onsets < 0.1 s excluded; at least 3), minus the onset bias of the model's constriction shape for each candidate τ. Otherwise fitted | `fit.onset_latency`, `fit.latency_from_onset` |
| 9.4 | Dynamics, offset | Nelder–Mead over log `attack` (0.3–30 s), log `release` (0.05–5 s) and optionally (the app: whenever it fits the dynamics) log `transient` (0.01–3 mm) and log `escape` (0.3–30 s); a transient at its lower limit is set to 0; the window has 30 s of pre-roll; the pupil scale and, by default, the offset are not fitted (with `fit_offset` the offset is the mean of expected − measured, and `alignment` = fixed is set) | `fit.fit_calibration` |

Glasses without a calibration sequence can still use a camera calibration:
`pipeline.calibrate_camera` sets `camera_white` from a fixed-exposure recording with a lux log (median of
\(\bar L / Y_\text{frame}\) over samples that are neither black nor saturated; a warning above ×2 spread).

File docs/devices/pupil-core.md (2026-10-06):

# Pupil Core

Pupil Labs Pupil Core recordings, exported with Pupil Player. Reader: `cwtool/devices/pupil_core.py`.

## Folder

```text
recording/
├── info.player.json          # start times (system and Pupil clock)
├── world.mp4                 # scene video
├── world_timestamps.npy      # capture time of each frame (Pupil clock)
├── world.intrinsics          # scene camera matrix (msgpack)
├── exports/
│   └── 000/                  # the newest numbered export is used
│       ├── pupil_positions.csv
│       └── gaze_positions.csv
├── 4_14_10.csv               # lux logs (or lux.csv), here or in lux/
└── <date>_event_log.csv      # optional
```

Export the recording in Pupil Player first (with the Raw Data Exporter enabled).

## Pupil

- **3D model** (`diameter_3d`, mm) when the export has 3D rows; otherwise the **2D** ellipse diameter (`diameter`,
  eye camera pixels). Older exports without 2D rows carry the pixel diameter in their 3D rows, which is used.
- Samples with confidence below **0.6** (Pupil Labs' recommendation) are dropped.
- `eye0` is the right eye, `eye1` the left. The two eyes are sampled independently, so both are averaged into bins
  on a common grid at their nominal rate.

Pixel diameters have no known scale: the pipeline scales them so the mean measured pupil equals the mean expected
pupil, as in the 2021 paper. The calibration fit is not available for pixel data.

## Gaze

`gaze_positions.csv` `norm_pos_x/y` (confidence ≥ 0.6), with y flipped to put the origin at the top left. Samples
more than 5 % outside the frame are dropped.

## Time

Time zero is the first scene frame; `epoch_start = start_time_system_s + (first frame − start_time_synced_s)`. Scene
frames are matched to gaze samples by their recorded timestamps, taking the **nearest** frame as Pupil Player does
(this reproduces Player's `world_index` for every sample of the test recording; a fixed frame rate was off by up to
24 frames because the camera drops frames).

## Scene camera

The field of view comes from `world.intrinsics`, with the lens distortion taken into account: the angle between the
middles of opposite edges of the frame. For the 1280×720 wide-angle lens this gives 103° × 54°, the values Pupil Labs
list (a pinhole model would give only 78° × 49°, the view near the centre); without the file those values are used.
It converts the gaze circle radius from degrees to pixels. The eye, however, adapts
to the whole binocular field, so the adapting field area uses 200° × 135° (Pignoni et al. 2021).

## Luminance

From the lux sensor worn on the tracker, distributed over the view with the scene video; see
[Luminance](../processing/luminance.md#lux-sensor-devices). Without lux logs the scene camera is used alone: as
relative luminance, with a warning, or, if the recording was made with manual exposure in Pupil Capture, as
absolute luminance with **Camera exposure** set to `fixed` (see
[Lux devices without a lux log](../processing/luminance.md#lux-devices-without-a-lux-log)).

## Profile

| | |
|---|---|
| Pupil | mm (scale 1) or px (fitted) |
| Luminance | lux sensor |
| Field of view | from the camera matrix; adapting field 200° × 135° |
| Circular scene | no |
| Rate | measured (120 or 200 Hz) |

## Differences from 1.x

Version 1.x pooled both eyes' pixel diameters into one series; 2.0 keeps the eyes separate and prefers the 3D
diameter in mm ([open issue 30](../OPEN_ISSUES.md)). It also combines the lux sensor and the video as published in
the 2021 paper rather than 1.x's heuristic ([open issue 29](../OPEN_ISSUES.md)).

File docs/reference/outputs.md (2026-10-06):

# Output files

## Export

Written by **File → Export results…** or `cwtool` (default folder `RECORDING/cwtool_export`) as one package: every
file below is cut to the same [export range](../usage/gui.md#export-range) and sensor files from the
[sensor logger](../usage/logger.md) go in with the results. `<name>` is the recording folder's name.

A **trim** (start, end, left-out segments) removes rows from every file by their time: a row is kept when its time is
at or after the start, at or before the end, and not inside a left-out segment (a segment includes its start and not
its end). The analysis itself always uses the whole recording.

!!! note "ΔPD in SD units after trimming"
    `delta_pd_sd` is ΔPD divided by the SD of ΔPD over the recording. With a trim it is divided by the SD of the
    ΔPD that is kept, so the values do not depend on what was left out. `<name>_export.json` says which was used.

### `<name>_pupil.csv`

One row per analysis grid sample (default 100 Hz).

| Column | Unit | Content |
|---|---|---|
| `timestamp_unix` | s | Unix time |
| `timestamp_relative` | s | from the first scene frame |
| `luminance_cdm2` | cd/m² | estimated luminance (only relative for a glasses recording without lux log and with automatic exposure) |
| `pupil_measured_mm` | mm | measured pupil, smoothed, scaled and offset; empty in long gaps |
| `pupil_measured_raw_mm` | mm | the same, lightly smoothed |
| `pupil_expected_mm` | mm | expected pupil |

### `<name>_cw.csv`

One row per ΔPD window (default 0.2 s).

| Column | Unit | Content |
|---|---|---|
| `timestamp_unix`, `timestamp_relative` | s | window centre |
| `delta_pd_mm` | mm | ΔPD |
| `delta_pd_sd` | SD | ΔPD / SD of ΔPD over the recording |

### `<name>_events.csv`

Only when the recording has events (and, with a trim, events with some of their time kept). An event is clipped to
the start and end, and its mean ΔPD is taken over the ΔPD windows that are kept; an event that is left out entirely
is not listed.

| Column | Content |
|---|---|
| `event` | label |
| `start_relative`, `end_relative` | s |
| `mean_delta_pd_mm`, `mean_delta_pd_sd` | mean ΔPD within the event |

### `<name>_lux.csv`

Only with a lux log: `timestamp_unix`, `timestamp_relative`, `lux` (the readings as logged), within the recording.

### `<name>_<sensor>.csv`

One file for each imported sensor file (`<name>_shimmer.csv`, `<name>_emotibit.csv`), within the recording and the
export range. The first two columns are `timestamp_unix` and `timestamp_relative` (the same axis as the files above);
the rest are the logger file's own columns, raw as logged: the Shimmer's channels in ADC counts plus its
`device time (s)`, or the EmotiBit's `signal` and `value`. See [Sensor logger](../usage/logger.md#what-is-saved).

### `<name>_params.json`

The parameters used, loadable as a participant file.

### `<name>_export.json`

What the package holds, for whoever receives it: the recording and device, the meaning of the time columns and the
Unix time of time zero, the trim (or `null`), the seconds kept, which SD was used for `delta_pd_sd` and its value, each
sensor file with its source, columns and row count, the list of files and the version of `cwtool`.

### `<name>_plot.pdf`

Measured vs expected pupil and ΔPD (needs matplotlib; `--plot` on the command line). The parts the trim leaves
out are shaded grey.

## Video cache

Written next to the recording after the video pass.

- `cwtool_video.csv`: one row per analysed gaze sample: `time`, mean 8-bit colour of the gaze circle (`fix_r/g/b`)
  and background (`bg_r/g/b`), then linear means `<area>_lin<γ>_<channel>` for the gaze circle (`fix`), background
  (`bg`) and whole visible scene (`frame`) at each γ of the grid.
- `cwtool_video.json`: what the cache was made from: format version, gamma grid, video settings, video file name,
  a hash of the frame timestamps and a hash of the gaze samples. The cache is used only if all match.

Delete both files to force a new analysis, or use `--reanalyse` / **Analyse video**.

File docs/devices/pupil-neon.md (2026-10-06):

# Pupil Neon

Pupil Labs Neon recordings. Reader: `cwtool/devices/neon.py`.

!!! warning "Not yet tested on a real recording"
    The reader was written from Pupil Labs' published data format and the `pl-neon-recording` library
    (September 2026) and is tested on synthetic recordings only. [Open issue 32](../OPEN_ISSUES.md) lists what a
    real recording must confirm. Until then every result carries a warning saying the support is experimental.

Two layouts are read. Prefer the Pupil Cloud export: it has pupil diameters and blinks computed at the full 200 Hz
even when the phone could not keep up in real time.

## Pupil Cloud "Timeseries Data + Scene Video"

Download the recording from Pupil Cloud as **Timeseries Data + Scene Video** and open the recording's folder.

```text
<recording name>-<id>/
├── info.json                 # start_time (UTC ns), gaze_mode, versions
├── 3d_eye_states.csv         # pupil diameter left/right [mm], 200 Hz
├── gaze.csv                  # gaze x/y [px], worn
├── blinks.csv
├── events.csv
├── world_timestamps.csv      # frame timestamps [ns]
├── scene_camera.json         # camera matrix, distortion
├── <section id>_<start>-<end>.mp4
└── 4_14_10.csv               # lux logs (or lux.csv), here or in lux/
```

| Used for | File and column |
|---|---|
| pupil | `3d_eye_states.csv`: `pupil diameter left [mm]`, `pupil diameter right [mm]` (older exports: `pupil diameter [mm]`, used for both eyes) |
| gaze | `gaze.csv`: `gaze x [px]`, `gaze y [px]`, divided by the video's size |
| not worn | `gaze.csv`: `worn` = 0 |
| blinks | `blinks.csv`: `start timestamp [ns]`, `end timestamp [ns]` |
| frame times | `world_timestamps.csv`: `timestamp [ns]` |
| events | `events.csv`: `timestamp [ns]`, `name` |
| field of view | `scene_camera.json`: `camera_matrix` |

With several sections (recording paused and resumed), the longest section and its video are analysed.

## Native recording format

The folder copied from the Companion phone over USB, or downloaded from Pupil Cloud as "Native Recording Data".
Each stream is a binary `<name> ps<n>.raw` with a `<name> ps<n>.time` file of int64 UTC nanoseconds.

| Used for | Files |
|---|---|
| pupil | `eye_state ps*.raw` (float32 records; left diameter first, right diameter at field 7, or by name from `eye_state.dtype`) |
| gaze | `gaze_200hz.raw` / `.time` if present, else `gaze ps*.raw` |
| not worn | `worn_200hz.raw` or `worn ps*.raw` (on the gaze timestamps) |
| events | `event.txt` / `event.time` |
| scene video | `Neon Scene Camera v1 ps*.mp4` / `.time` (the longest part) |
| field of view | `calibration.bin` (scene camera matrix) |

!!! note "Pupil diameters need eye state estimation"
    The native format has pupil diameters only if real-time eye state estimation was enabled in the Companion app.
    Otherwise the reader stops with an explanation: upload the recording to Pupil Cloud and use the Timeseries
    export instead. Blinks are not in the native format; the pipeline's speed filter removes their edges.

## Processing

- Pupil diameters are in mm (scale 1), each eye separately. Zero or missing values are invalid.
- Samples where Neon was not worn lose their pupil and gaze values; Cloud blinks remove the pupil from 0.1 s
  before to 0.1 s after each blink.
- Samples are averaged into bins on a grid at the measured rate (nominally 200 Hz).
- Time zero is the first scene frame; the eye cameras start slightly earlier, so the recording can start at
  negative times.

## Events

Neon events are instants. They are turned into intervals as follows:

- `recording.begin` and `recording.end`, which Neon adds to every recording, are ignored.
- Pairs named `<label>.begin` / `<label>.end` (also `_start`/`_stop`, `onset`/`offset`, with `.`, `_`, `-` or a
  space) become one event `<label>`.
- Any other event starts a phase that lasts until the next such event, or the end of the recording.

An `event_log` CSV from the [event logger](../usage/tools.md#event-logger) in the folder is read as well.

## Scene camera exposure

Neon's scene camera can run with **manual exposure** (1–1000 ms, set in the Companion app's preview), or one of
three automatic modes. Automatic exposure rescales the video's brightness with the scene, so the video can only
distribute the lux sensor's reading over the view (which is how it is used), not measure luminance itself.

With **manual exposure** the video is photometrically stable, and it can stand in for the lux sensor: set
**Camera exposure** to `fixed` and enter the exposure time. Calibrate the camera's full-scale luminance once on a
recording made with the lux sensor (see
[Lux devices without a lux log](../processing/luminance.md#lux-devices-without-a-lux-log)). Exposures above 330 ms
lower the frame rate below 30 fps.

## Clocks

Neon's timestamps come from the Companion phone's clock, the lux logger's from the computer (or the SD logger's
real-time clock). Pupil Labs report offsets under 10 ms between freshly synced clocks, growing to about 1 s after
24 hours. Before a session, force both to resync with the time server, as Pupil Labs recommend:

- **Phone:** *Settings → System → Date & time*, turn off *Set time automatically*, move the time by one hour, wait
  5 seconds, turn it back on.
- **Computer running the lux logger:** the same in the system's date and time settings (on macOS then run
  `sudo sntp -sS time.apple.com`).

Any remaining offset shifts the luminance against the pupil and can be corrected with the **time lag** parameter
([open issue 34](../OPEN_ISSUES.md)). A light switched on in front of both the sensor and the scene camera gives a
visible mark to measure it.

## Profile

| | |
|---|---|
| Pupil | mm, scale 1 |
| Luminance | lux sensor, distributed with the scene video |
| Field of view | from the camera matrix (nominal 103° × 77°); adapting field 200° × 135° |
| Circular scene | no |
| Rate | measured (nominally 200 Hz) |

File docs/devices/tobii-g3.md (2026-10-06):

# Tobii Pro Glasses 3

!!! warning "Experimental support"
    The reader (`cwtool/devices/tobii_g3.py`) was written from the 1.x Tobii branch (`legacy-TobiiProIII`,
    2022) and Tobii's recording format, and is tested on synthetic recordings only. Every result carries a warning
    until a real recording has confirmed it. [Open issue 45](../OPEN_ISSUES.md) lists what to check.

## Folder

Copy the recording folder from the recording unit's SD card:

```text
<recording>/
├── recording.g3        # JSON: created (UTC start), duration, stream files, scene camera calibration
├── gazedata.gz         # gaze and pupil, one JSON object per line
├── eventdata.gz        # events (optional)
├── scenevideo.mp4      # scene camera
├── 9_28_10.csv         # lux logs (or lux.csv), here or in lux/
└── <date>_event_log.csv  # optional, from tools/event_logger.py
```

## What is read

| Used for | Source |
|---|---|
| start time | `recording.g3` → `created` (UTC); the recording start is taken as the start of the scene video. Without it the lux log and event logs cannot be matched and are not read (a note says so; exported Unix times are empty): the file's modification time would be the copy time after an SD card transfer |
| time zone | `recording.g3` → `timezone` (IANA name, as used by 1.x): event logs without a zone are read in it |
| pupil | `gazedata.gz` → `data.eyeleft.pupildiameter`, `data.eyeright.pupildiameter` (mm) |
| gaze | `gazedata.gz` → `data.gaze2d`, normalised scene video coordinates, origin top left |
| invalid samples | samples with empty `data`; each eye separately, so a sample with one eye tracked still counts for that eye |
| scene video | `recording.g3` → `scenecamera.file` (default `scenevideo.mp4`), frames timed by its frame rate |
| field of view | `recording.g3` → `scenecamera.camera-calibration` (focal length, resolution) with a pinhole model, else the nominal 95° × 63° |
| events | `eventdata.gz` entries of type `event`, named by their `tag` (other types, such as `syncport`, are ignored); an `event_log` CSV is read as well |

Events are turned into intervals as for the Neon: `<label>.begin` / `<label>.end` pairs become one event, other
events last until the next one.

Differences from 1.x: 1.x kept only samples with both pupils, and flipped gaze y (`1 − y`), which suits the Pupil
Core's coordinates, not Tobii's. 2.0 keeps each eye separately and does not flip; `load(..., flip_gaze_y=True)`
reproduces the 1.x behaviour if a real recording shows the flip was right.

## Luminance

Like the other glasses, the Glasses 3 is used with the external [lux sensor](../hardware/lux-sensor.md), distributed
over the view with the scene video; without lux logs the camera is used alone
([Luminance](../processing/luminance.md#lux-devices-without-a-lux-log)).

## Profile

| | |
|---|---|
| Support | experimental |
| Pupil | mm, scale 1 |
| Luminance | lux sensor |
| Field of view | from the camera calibration (nominal 95° × 63°); adapting field 200° × 135° |
| Circular scene | no |
| Rate | measured (50 Hz, or 100 Hz if set on the unit) |

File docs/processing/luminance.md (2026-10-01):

# Luminance

How the video pass's colours become the luminance \(L(t)\) in cd/m² that drives the pupil model. Which method is
used depends on the device profile's `luminance_source`.

## Colour to linear light

Code values \(C\) (0–255) are decoded with a power curve,

\[
C_\text{lin} = \left(\frac{C}{255}\right)^{\gamma}
\]

per pixel, before averaging (see [Scene video analysis](video.md#linearising-before-averaging)). At \(\gamma\) = 2.2
this is the usual approximation of the sRGB curve; unlike the piecewise sRGB formula it stays continuous for any
\(\gamma\), which is adjustable because headset tone mapping is undocumented.

The gaze circle and background means are then weighted, with \(w\) = `fixation_weight` (default 0.26, Eckert et al. 2022):

\[
\mathbf{C}_w = w\,\mathbf{C}_\text{lin,gaze} + (1 - w)\,\mathbf{C}_\text{lin,background}
\]

(`VideoResult.weighted`, used by every luminance method and by the calibration fit.)

## Display devices

For the Varjo, the capture shows what the display showed, so the colours map to luminance through the
**display photometry** (the per-channel extension of the WCAG 2.1 relative luminance proposed in the Varjo manuscript,
[in preparation](../reference/references.md)):

\[
L = \sum_{c \in \{R,G,B\}} k_c \left( L_\text{max}\, \frac{g_c}{\bar g}\, C_{w,c} + L_\text{min}\,(1 - C_{w,c}) \right)
\]

- \(L_\text{min}\), \(L_\text{max}\): the panel's black and white points (cd/m²), parameters `l_min`, `l_max`;
- \(g_c\): channel gains (`gain_r/g/b`), divided by their mean \(\bar g\) so they act as a relative balance;
- \(k_c\) = 0.2126, 0.7152, 0.0722: the photopic weights of the BT.709/sRGB primaries.

**Change from the manuscript (September 2026).** The manuscript divides the whole sum by \(\bar g\), black-point term included:
\(L = \frac{1}{\bar g}\sum_c k_c (L_\text{max} g_c C_{w,c} + L_\text{min}(1 - C_{w,c}))\). Black then maps to
\(L_\text{min}/\bar g\) rather than \(L_\text{min}\) whenever the gains do not average 1, and the manuscript's statement that
uniform gains reduce to the plain linear mapping holds only for gains of 1. In the calibration fit the gains are free,
so their overall scale also changed the black level during the fit, and normalising the reported weights to a mean of
1 afterwards changed it again. 2.0 applies the gains to the white-point term only: black is always \(L_\text{min}\),
and scaling all gains by a constant changes nothing ([open issue 9](../OPEN_ISSUES.md)).

With unit gains this is a linear mapping of relative luminance onto \([L_\text{min}, L_\text{max}]\). These are
real luminances: the adapting field area comes from the device profile. \(L_\text{min}\), \(L_\text{max}\) and
\(\gamma\) are the user's nominal values for the headset (e.g. its datasheet), saved in their own file; the defaults
(0.01 and 100 cd/m²) are a nominal white and the black from the datasheet's 10000:1 contrast; the app warns when Lmax is more than 10 % above the device's claimed peak luminance (200 cd/m² for the Varjo), when Lmin is not below Lmax, or when the contrast is below 100:1 ([open issue 48](../OPEN_ISSUES.md)). The channel gains are the participant's channel
weights, fitted with their light sensitivity on the [calibration sequence](../usage/calibration.md).

## Lux sensor devices

For the Pupil Core, Neon and Tobii Pro Glasses 3, the scene camera's automatic exposure hides the absolute level, so it comes from the
[lux sensor](../hardware/lux-sensor.md). Following Pignoni et al. (2021, eq. 5–8):

1. The lux readings are smoothed (Savitzky–Golay, 11 samples, order 6) and converted to the **average luminance**
   of the sensor's view: \(\bar L = (g \cdot E + o) / \Omega\) (parameters `lux_gain`, `lux_offset`,
   `lux_solid_angle`). \(\Omega\) = 2.2 is the ratio of illuminance to average luminance for the sensor in its
   housing, and \(g\) = 1, \(o\) = 0 by default (1.x used 1.706061 and 0.66935; see
   [Lux sensor](../hardware/lux-sensor.md)).
2. The video **distributes** that average over the view. With \(Y_w\) the relative luminance of the weighted
   gaze/background colour and \(Y_\text{frame}\) that of the whole frame, both computed with the photopic weights
   and channel balance:

\[
L = \bar L \cdot \frac{Y_w}{Y_\text{frame}}
\]

Looking at something brighter than the average of the view raises \(L\) above the sensor's average, and vice versa.
The camera's exposure cancels in the ratio. Set `lux_use_video` off to use the sensor's average alone.

The ratio follows where the gaze looks, and it is not always right to keep it. It is what carries the changing
screen into the luminance when the sensor sees little of it (a laptop screen filling part of the view, the sensor
looking past it), but on a uniform view it should stay near 1 and it only adds noise when it wanders, as it does on
dark frames. The analysis flags a wide spread (10th to 90th percentile above ×1.5, frames that are not nearly
black), which is a prompt to compare the two settings, not a verdict: two calibration recordings on a screen gave
opposite answers. The app
plots the sensor average, the luminance used and the ratio, so the effect of the video can be seen.

In the 2021 paper the area of interest was selected around the gaze with a Grab Cut algorithm and used alone
(\(L = \bar L \cdot rL_\text{AOI} / rL_\text{frame}\)). 2.0 uses the fixed gaze circle weighted against the background,
as for the display devices, so \(Y_w\) replaces \(rL_\text{AOI}\).

\(L_\text{min}\) and \(L_\text{max}\) are not used in this mode, so the plots show no black and white point lines.

Version 1.x combined the sensor and camera with a different heuristic; see [open issue 29](../OPEN_ISSUES.md).

## Lux devices without a lux log

If a glasses recording has no lux readings, the scene camera is used alone. **Camera exposure** (`camera_exposure`)
says how to read it.

**`auto`** (default): the camera adjusted its exposure, so the video gives only relative luminance. It is mapped onto
\([L_\text{min}, L_\text{max}]\) as for a display, and a warning says so.

**`fixed`**: the exposure was fixed during the recording (Neon's manual exposure mode, or manual exposure in Pupil
Capture for the Core). Linearised pixel values are then proportional to scene luminance, up to saturation:

\[
L = L_\text{full} \cdot Y_w, \qquad L_\text{full} = L_\text{white} \cdot \frac{t_\text{ref}}{t}
\]

- \(Y_w\): relative luminance of the weighted gaze/background colour, as above;
- \(L_\text{white}\) (`camera_white`): the luminance that saturates the camera (code 255) at the reference
  exposure time \(t_\text{ref}\) (`camera_reference_ms`);
- \(t\) (`camera_exposure_ms`): the recording's exposure time. A longer exposure saturates at a lower luminance.
  With either time at 0, \(L_\text{white}\) is used as is.

A warning appears when the gaze area is saturated (mean code value ≥ 250) in more than 5 % of the video samples,
since luminance is underestimated there.

### Calibrating the camera from a lux log

\(L_\text{white}\) depends on the camera, its gain and the lens, so it is measured once: record with the same
fixed exposure **and** the lux sensor, open that recording, enter its exposure time and click
**Calibrate camera from lux**. The sensor's average luminance \(\bar L\) and the whole frame's relative luminance
\(Y_\text{frame}\) describe the same view, so

\[
L_\text{white} = \operatorname{median}\left(\frac{\bar L}{Y_\text{frame}}\right)
\]

over the video samples that are neither black nor saturated. The dialog reports the spread (90th / 10th percentile
of the per-sample ratios); above ×2 it warns that the exposure was probably not fixed. Applying sets `camera_white`
and `camera_reference_ms`; save the parameters and load them for recordings without a lux log.

The assumptions behind this (fixed gain, the camera's tone curve, lens vignetting) are listed in
[open issue 35](../OPEN_ISSUES.md).

## Timing

The video and lux luminance are interpolated onto the analysis grid, shifted by the **time lag** parameter
(`timelag`, s, subtracted from the luminance timestamps).

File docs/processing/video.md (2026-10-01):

# Scene video analysis

`cwtool/video.py`. For every valid gaze sample, the frame shown at that moment is measured in two areas:

- the **gaze circle** (fixation area): a disc of `fixation_radius_deg` (default 16.35°) around the gaze point,
  limited to the visible scene (near the edge of a circular capture it does not take in the black corners);
- the **background**: the rest of the visible scene. On circular Varjo captures the visible scene is a centred
  circle of `field_radius` × half the frame height (default 0.8), which excludes the black corners; on other
  devices it is the whole frame. By default the gaze circle is removed from the background
  (`background_excludes_fixation`), as in the Varjo manuscript (in preparation) and Eckert et al.

The luminance used later is a weighted sum of the two (default 26 % gaze circle, 74 % background).
The default radius and weights are those of Eckert et al. (2022): a radius of 14.8 % of their headset's display
diagonal (16.35°), and the weights their grid search found best on their VR scenes (MAE 0.31 mm)
(1.x used 5.25° and 65 %); they are a reference value, not a calibration for each device (open issue 47).

## Geometry

Frames are downscaled to `analysis_width` (500 px) before measuring. The gaze circle's radius in pixels is

\[
r = \frac{\text{fixation\_radius\_deg}}{\text{vertical field of view}} \cdot h
\]

with \(h\) the analysed frame height and the vertical field of view from the device profile. This assumes a linear
lens mapping ([open issue 33](../OPEN_ISSUES.md) for the wide-angle cameras of glasses trackers). The 1.x default,
5.25°, was 1/8 of the scene circle on the Varjo XR-4; on a glasses scene camera with about 54° of vertical view
the 16.35° circle spans about 60 % of the frame height.

## Linearising before averaging

Video code values are gamma-encoded. The mean of a textured area must be taken on linear values: the mean of
\((C/255)^\gamma\), not the mean code value raised to \(\gamma\). A black-and-white checkerboard, for example, has a
mean code value of 128, which decodes to 22 % of white, while its real mean luminance is 50 %.

So that gamma can still change in the app without re-reading the video, each area's per-channel histogram is turned
into linear means for every gamma on a grid (1.4 to 3.0 in steps of 0.2). The signal pass interpolates between grid
points in log space, with an error below 0.001 of full scale. Frames are downscaled with nearest-neighbour sampling
for the same reason: it keeps real pixel values instead of averaging code values.

Per sample the pass stores the mean 8-bit colour of each area (for display), the linear means of the gaze circle,
the background and the whole visible scene for each gamma.

## Matching gaze samples to frames

- Devices with **recorded frame timestamps** (Pupil Core, Neon): each gaze sample uses the frame whose timestamp is
  nearest, as Pupil Player does. Scene cameras drop frames, so a fixed frame rate would drift.
- Devices with a **constant frame rate** (Varjo, Tobii Pro Glasses 3): frame \(n\) covers \([n/\text{fps}, (n+1)/\text{fps})\).

Samples outside the video, or with invalid gaze, are skipped.

## Speed

Every frame has to be decoded (compressed video needs it), but only frames with gaze samples are converted and
measured.

- Decoding uses PyAV, which scales and converts to RGB inside FFmpeg with its own threads; OpenCV is the fallback.
- The frame range is split into chunks (at least 150 frames each, one per CPU core by default) decoded in parallel
  threads. The result does not depend on the number of chunks.
- Frames are numbered by their presentation timestamps, so chunk seeks land on exactly the right frame.

For reference: 251 s of 4K H.264 Varjo capture in 49 s on 4 cores; 100 s of Pupil Core world video in about 15 s.

## Cache

The result is saved as `cwtool_video.csv` with `cwtool_video.json` next to the recording. It is reused only if the
format version, gamma grid, video settings, video file name, frame timestamps and gaze samples all match, so it is
never silently stale. See [Output files](../reference/outputs.md#video-cache).

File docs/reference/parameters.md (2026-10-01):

# Parameters

Two sets, both in `cwtool/params.py`.

- **`Parameters`**: everything applied after the video pass. Saved per participant as JSON from the app
  (**File → Save parameters**) and loaded with `--params`. Changing them re-runs only the fast signal pass.
- **`VideoSettings`**: the geometry of the video pass. Changing them requires re-analysing the video.

## Participant

| Name | Default | Meaning |
|---|---|---|
| `age` | 25 | participant's age (years), for Watson & Yellott |
| `eyes` | 2 | eyes adapted to the light (1 or 2) |
| `eye` | both | pupil analysed: `left`, `right` or `both` |

## Display photometry (display devices)

The headset's nominal values, e.g. from its datasheet. Saved in their own file (**File → Save display photometry…**),
not in participant files.

| Name | Default | Meaning |
|---|---|---|
| `l_min` | 0.01 cd/m² | panel black point (white over the datasheet's 10000:1 contrast) |
| `l_max` | 100 cd/m² | panel white point; warned about above 110 % of the device's claimed peak (Varjo: 200 cd/m²), [open issue 48](../OPEN_ISSUES.md) |
| `gamma` | 2.2 | decoding exponent, 1.4–3.0 |

## Participant light response

| Name | Default | Meaning |
|---|---|---|
| `sensitivity` | 1 | factor on the luminance entering Watson & Yellott; also absorbs common errors of the display photometry (fitted) |
| `gain_r`, `gain_g`, `gain_b` | 1 | channel weights for the pupil, normalised by their mean (fitted) |
| `fixation_weight` | 0.26 | weight of the gaze circle (Eckert et al. 2022; 1.x used 0.65); the background gets 1 − weight (also used with lux devices) |

## Lux sensor (glasses)

| Name | Default | Meaning |
|---|---|---|
| `lux_gain` | 1 | recalibration of the sensor's lux (1.x: 1.706061, a field-of-view correction from one test) |
| `lux_offset` | 0 | recalibration offset, lux (1.x: 0.66935) |
| `lux_solid_angle` | 2.2 | illuminance / average luminance ("Lux ÷ luminance (Ω)" in the app) for the sensor in its housing (not a solid angle; see [Lux sensor](../hardware/lux-sensor.md)) |
| `lux_use_video` | on | distribute the sensor's average over the view with the scene video |
| `lux_ratio_limit` | 10 | the video ratio (gaze-weighted / whole frame) is kept between 1/limit and limit ("Max video ratio"); 0 = no bound. A note says when it is reached in more than 5 % of the video samples |

## Scene camera without a lux log (glasses)

| Name | Default | Meaning |
|---|---|---|
| `camera_exposure` | auto | `auto`: relative luminance mapped onto Lmin–Lmax; `fixed`: the exposure was fixed, pixel values are proportional to luminance |
| `camera_white` | 1000 cd/m² | luminance at full scale (code 255) for the reference exposure; set it with **Calibrate camera from lux** |
| `camera_reference_ms` | 0 | exposure time `camera_white` refers to; 0 = the recording's |
| `camera_exposure_ms` | 0 | the recording's exposure time; full scale is scaled by reference / recording; 0 = same as the reference |

## Pupil signal

| Name | Default | Meaning |
|---|---|---|
| `pupil_correction` | 1 | participant multiplier on the device's pupil scale, set by hand and never fitted: one sequence does not determine it (it trades off with the sensitivity and the black point) |
| `alignment` | recording | offset mode: `recording`, `baseline`, `fixed`, `none` |
| `baseline_events` | Riposo, Rest, Baseline | event labels used by `baseline` alignment |
| `pupil_offset` | 0 mm | offset used by `fixed` alignment (set by hand; the fits leave it alone unless asked) |
| `timelag` | 0 s | subtracted from luminance timestamps (video and lux) |
| `analysis_rate` | 100 Hz | uniform grid rate; 0 = the device's native rate |
| `max_gap` | 0.5 s | longer gaps are left out of ΔPD |
| `max_pupil_speed` | 10 mm/s | faster changes are artefacts; 0 disables |
| `artefact_padding` | 0.05 s | removed around each artefact |

## Dynamics

| Name | Default | Meaning |
|---|---|---|
| `delay` | 0.5 s | response latency, always applied (fitted) |
| `dynamics` | on | apply the dynamics: attack/release filter, constriction stages and transient |
| `attack` | 6 s | dilation time constant (fitted) |
| `release` | 0.5 s | constriction time constant, per stage (fitted) |
| `constriction_stages` | 2 | 1: constriction starts at full speed; 2: gradually (S-shaped); files without it load as 1 |
| `transient` | 0 mm | largest transient constriction after brightening, with the dynamics; 0 = none (fitted) |
| `escape` | 2 s | re-dilation time constant of the transient (fitted) |

## ΔPD

| Name | Default | Meaning |
|---|---|---|
| `cw_window` | 0.2 s | averaging window |
| `cw_smoothing` | 1 | Savitzky–Golay half-width, in windows |

## Video settings

| Name | Default | Meaning |
|---|---|---|
| `fixation_radius_deg` | 16.35° | gaze circle radius (Eckert et al. 2022; 1.x used 5.25°) |
| `field_radius` | 0.8 | scene circle radius as a fraction of half the frame height (circular videos) |
| `background_excludes_fixation` | on | remove the gaze circle from the background |
| `analysis_width` | 500 px | frames are downscaled to this width |
| `circular_mask`, `vertical_fov` | from the device | set automatically from the recording |

## File format and older files

A participant file is the JSON of `Parameters` without the display photometry, with a `version` field (currently 3).
Loading one keeps the display photometry in use; files that do contain `l_min`, `l_max` or `gamma` (older ones, and
the parameters written with an export, which record everything used) set them too.

A display photometry file holds `kind` ("cwtool display photometry"), `device`, `l_min`, `l_max`, `gamma` and a free
`source` text.

Files from version 1.x are converted on load:

- `field` (the adapting field value used directly in the flux) is removed and `l_min`, `l_max` are rescaled by
  `field / device field area`, which gives identical expected pupils;
- the absolute `pupil_scale` becomes `pupil_correction` relative to the device's scale;
- `align_mean` becomes `alignment` (`recording` or `none`).

Unknown fields are ignored, so files stay readable as parameters are added.

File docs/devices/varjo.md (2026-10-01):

# Varjo XR-4

Recordings from Varjo Base's eye tracking recorder. Reader: `cwtool/devices/varjo.py`. Checked against a Varjo
Base export from April 2026.

## Folder

```text
recording/
├── varjo_gaze_output_<date>.csv     # eye tracking, 200 Hz
├── varjo_capture_<date>.mp4         # capture of the left-eye view
└── <date>_event_log.csv             # optional, from tools/event_logger.py
```

## Gaze CSV

Columns are found by header name, falling back to the positions of the pilot study's export for files without a
header. Values written as `-nan(ind)` (Varjo Base on Windows) are read as missing.

| Used for | Column |
|---|---|
| time (video clock) | `relative_to_video_first_frame_timestamp` (ns) |
| Unix time | `relative_to_unix_epoch_timestamp` (ns) |
| validity | `status`, `left_status`, `right_status` (tracked when > 1; Varjo writes 0 = lost, 2 = tracked) |
| pupil | `left_pupil_diameter_in_mm`, `right_pupil_diameter_in_mm` |
| gaze | `gaze_projected_to_left_view_x/y` (default), or `left_projected_x/y`, `right_projected_x/y` |

Each eye's pupil is valid where that eye's status is tracked and the gaze `status` too, so a sample with one eye
lost keeps the other (the pipeline bridges the missing eye). The gaze is valid where its eye is tracked (for the
combined gaze, either eye).

## Pupil scale

Older Varjo Base versions write the pupil **radius** in its diameter columns (confirmed by Varjo by email), so the
pupil scale is 2. Their iris diameter column reads a constant 6.04 mm, half a typical iris, which fits. A later
version (a September 2026 sample) writes real diameters: the iris column reads a constant 12.2–12.5 mm and the
pupil–iris ratio matches. The reader tells the two apart by the median iris diameter (above 9 mm: diameters, scale 1;
below, or unreadable: radii, scale 2), so each recording gets its own scale; the Recording box shows it. The calibration fits do not
estimate the pupil scale: one sequence does not determine it, and the dark-adapted pupil of a recording (6.4–7.7 mm in
the September 2026 sample) bounds it to about 0.9–1.2, so the device's scale is used. A participant correction
(`pupil_correction`) can be set by hand ([open issue 1](../OPEN_ISSUES.md)).

## Gaze

The capture shows the **left eye's view**. The combined gaze projected to that view is used by default; the left
eye's own projection is available (`gaze_eye="left"`), the right eye's is in the right view and so offset from the
capture. Projected coordinates run from −1 to 1 with y up and are converted to 0–1 with y down.

## Scene video

H.264 at a steady 30 fps; the gaze timestamps are relative to its first frame, so frames are matched by frame
rate. The scene is a circle with black corners: the background area is a centred circle (radius 0.8 of half the
frame height by default) to exclude them.

## Profile

| | |
|---|---|
| Pupil | mm, scale 2.0 (radius export) or 1.0 (diameter export, from the iris column) |
| Luminance | display: the scene capture's colours mapped through the [display photometry](../processing/luminance.md#display-devices), with the participant's light sensitivity |
| Field of view | 120° × 105° (nominal); the adapting field is the same |
| Circular scene | yes |
| Rate | 200 Hz |

## Calibration

Each participant watches the full-field calibration sequence in the headset; see
[Participant calibration](../usage/calibration.md). In the April 2026 sample the sequence used 10 s steps starting
16.4 s into the recording, and "Find in recording" located it in 0.2 s.

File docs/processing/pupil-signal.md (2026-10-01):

# Pupil signal

`pipeline.prepare`. From the device's per-eye pupil values to a clean signal on a uniform grid.

## 1. Scale to mm

Device units × the profile's `pupil_scale` × the participant's `pupil_correction`. The Varjo reader sets the scale
per recording, 2 for exports that hold the radius and 1 for those that hold the diameter ([Varjo XR-4](../devices/varjo.md#pupil-scale)). For pixel data (Pupil Core 2D)
the scale is unknown and set later so the mean measured pupil equals the mean expected pupil (2021 method).

## 2. Range check

Scaled diameters outside **1–9 mm** are tracking errors and removed.

## 3. Artefact filter

Blink edges and tracking jumps change the apparent pupil faster than the iris can. A sample is removed when the
pupil changes faster than `max_pupil_speed` (default 10 mm/s) towards the previous or next sample **at least 40 ms
away**, and `artefact_padding` (0.05 s) is removed around each. Measuring the speed over 40 ms rather than between
neighbouring samples keeps the threshold independent of the sampling rate: at 200 Hz, sample-to-sample noise alone
would read as high speed. Physiological responses stay well below 10 mm/s. Set the speed to 0 to disable the filter.

Steps 2 and 3 run on each eye separately. Pixel data (Pupil Core 2D) skip both: their thresholds are in mm and the
scale is only known after the expected pupil is computed.

## 4. Combine the eyes

`eye` = `left`, `right` or `both`. `both` averages the two eyes. Where one eye is missing it is taken as the other plus
the median difference between the eyes, measured on the samples with both (at least 20; otherwise the tracked eye is
used as it is): the eyes often differ by a steady amount (up to 0.26 mm on the Varjo calibration recordings), and a
plain fallback would step the average by half of it whenever one eye drops out
([open issue 45](../OPEN_ISSUES.md)).

## 5. Resample

The signal is put on a uniform grid at `analysis_rate` (default 100 Hz; 0 = the device's native rate), by linear
interpolation between valid samples. Gaps longer than `max_gap` (0.5 s) are marked invalid: they are left out of
ΔPD, the offset and the statistics, and appear as breaks in the plots. Shorter gaps (blinks) are bridged. The
summary line reports the share of the recording in long gaps, together with the stretches where the luminance is
unknown ([Processing at a glance](pipeline.md), step 3d).

## 6. Smooth

Two Savitzky–Golay versions are kept:

| Signal | Window | Order | Use |
|---|---|---|---|
| measured | about 0.5 s | 2 | ΔPD, the black curve |
| measured (raw) | about 0.25 s (at least 9 samples) | 6 | the grey curve; the calibration fit, which needs step edges |

The measured pupil is then scaled (pixel data), offset ([ΔPD and alignment](delta-pd.md)) and compared with the
expected pupil.

## Plausibility

If the median measured pupil is outside 2–8 mm after scaling and the offset (as plotted and exported), a warning
suggests checking the pupil scale correction (set by hand) and the offset.

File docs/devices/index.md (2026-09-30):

# Devices

Each device has a reader in `cwtool/devices/` that turns a recording folder into the same device-independent
`Recording`. Everything after that, from the video analysis to ΔPD, is shared.

```mermaid
flowchart LR
    V[Varjo folder] --> RV[devices/varjo.py]
    C[Pupil Core folder + lux logs] --> RC[devices/pupil_core.py]
    N[Neon folder + lux logs] --> RN[devices/neon.py]
    T[Glasses 3 folder + lux logs] --> RT[devices/tobii_g3.py]
    RV --> R[(Recording + DeviceProfile)]
    RC --> R
    RN --> R
    RT --> R
    R --> P[shared pipeline]
```

## Detection

`devices.detect(folder)` asks each reader in turn whether it recognises the folder:

| Device | Recognised by |
|---|---|
| `varjo` | a file whose name contains `varjo_gaze_output_` |
| `pupil_core` | `info.player.json` and an `exports/<n>/pupil_positions.csv` |
| `pupil_neon` | `info.json` with `3d_eye_states.csv` or `gaze.csv` (Cloud export), or `gaze ps*.raw` / `gaze_200hz.raw` / `eye_state ps*.raw` (native) |
| `tobii_g3` | `recording.g3` and `gazedata.gz` |

Pass `--device` (or `device=` to `devices.load`) to skip detection.

## Comparison

| | Varjo XR-4 | Pupil Core | Pupil Neon | Tobii Pro Glasses 3 |
|---|---|---|---|---|
| Support | tested | tested | experimental | experimental |
| Pupil | mm: radius ×2 in older exports, diameter in newer ones (from the iris column) | mm (3D model) or px (2D) | mm per eye | mm per eye |
| Sampling | 200 Hz | 120/200 Hz per eye | 200 Hz | 50 or 100 Hz |
| Invalid samples | tracking status | confidence < 0.6 | not worn, blinks (Cloud) | empty samples, per eye |
| Gaze | projected to the left-eye view | normalised scene coordinates | scene camera pixels | normalised scene coordinates |
| Scene video | capture of the left-eye view, circular | world camera | scene camera, 1600×1200 | scene camera, 1920×1080 |
| Frame timing | constant frame rate | recorded timestamps | recorded timestamps | constant frame rate |
| Luminance | display photometry | lux sensor + video | lux sensor + video | lux sensor + video |
| Adapting field | display field of view | binocular visual field | binocular visual field | binocular visual field |
| Events | `event_log` CSV | `event_log` CSV | recording/Cloud events + `event_log` CSV | `eventdata.gz` + `event_log` CSV |

**Experimental** readers were written from the manufacturer's documentation and have not been checked on a real
recording. Every result from them carries a warning saying so (in the app's summary line and on the command line);
the open issue for each lists what a real recording must confirm.

## The Recording

Defined in `cwtool/recording.py`. All arrays share one time base.

| Field | Content |
|---|---|
| `time` | s, relative to the first scene video frame (can start below 0) |
| `epoch_start` | Unix time (s) of `time == 0`, used to find lux readings and write absolute timestamps |
| `pupil_left`, `pupil_right` | pupil size in the device's unit; NaN where invalid |
| `gaze` | (N, 2) normalised scene video coordinates, origin at the top left; NaN where invalid |
| `scene_video` | path of the scene video |
| `scene_frame_times` | recorded time of each frame (s, same clock), or None for a constant frame rate |
| `lux_time`, `lux_values` | lux sensor readings on the same clock, for lux devices |
| `events` | list of `Event(label, start, end)` |
| `profile` | the `DeviceProfile` |

## The DeviceProfile

What the analysis needs to know about a device, as opposed to a participant:

| Field | Use |
|---|---|
| `pupil_unit`, `pupil_scale` | device units × scale = mm; `None` for pixels (scaled per recording). The Varjo reader sets the scale per recording |
| `luminance_source` | `display` (display photometry) or `lux_sensor` |
| `field_of_view` | deg (h, v) spanned by the scene video: converts the gaze circle radius to pixels |
| `circular_scene` | the scene video is a circle with black corners that must be masked out (Varjo) |
| `native_rate` | Hz, used when `analysis_rate` is 0 |
| `adapting_field` | deg (h, v) the eye adapts to, if larger than the video; its area enters Watson & Yellott |
| `experimental` | the reader has not been checked on a real recording; results carry a warning |

Because each device supplies its own field area and pupil scale, the photometric parameters are real luminances
and parameter files are device-independent.

## Adding a device

Write a module in `cwtool/devices/` with:

```python
NAME = "my_tracker"

def detect(folder: Path) -> bool: ...

def load(folder: Path, **options) -> Recording: ...
```

and add it to `READERS` in `cwtool/devices/__init__.py`. `devices.load` passes only the options the reader's
`load` accepts (e.g. `lux_folder`), so readers can take their own. Helpers in `devices/common.py` cover binning
irregular samples onto a grid, estimating the sampling rate, the field of view from a camera matrix, reading event
logs and turning point markers into events. Add a synthetic recording writer to `tests/conftest.py` and tests like
`tests/test_neon.py`.

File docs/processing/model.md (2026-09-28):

# Expected pupil model

`cwtool/model.py`, `pipeline.expected_pupil`. The pupil diameter light alone would produce, in three stages.

## 1. Watson & Yellott (2012)

The unified formula for the light-adapted pupil. The corneal flux density is luminance × adapting field area ×
the monocular attenuation, with the participant's light sensitivity \(s\) (`sensitivity`, default 1) applied to
the luminance:

\[
F = s \cdot L \cdot a \cdot M(e), \qquad M(2) = 1,\; M(1) = 0.1
\]

with \(a\) the adapting field area in deg² (from the device profile, treating the field as an ellipse) and \(e\)
the number of eyes adapted (`eyes`). The sensitivity is fitted on the calibration sequence
([Calibration fit](calibration-fit.md#light-sensitivity)); the exported luminance is \(L\), without it. The Stanley & Davies (1995) diameter is

\[
D_{SD} = 7.75 - 5.75 \, \frac{(F/846)^{0.41}}{(F/846)^{0.41} + 2}
\]

corrected for the participant's age \(y\) (`age`) against the reference age \(y_0\) = 28.58 years, the mean age of the
observers behind the Stanley & Davies formula (a constant of the model, not a setting):

\[
D = D_{SD} + (y - y_0)(0.02132 - 0.009562\, D_{SD})
\]

Because \(F\) depends only on \(L \cdot a\), changing the field area is equivalent to rescaling
\(L_\text{min}\) and \(L_\text{max}\). This is how parameter files from 1.x, which used the field as a free value,
are converted exactly.

| Device | Adapting field | Area |
|---|---|---|
| Varjo XR-4 | 120° × 105° (display) | 9 896 deg² |
| Pupil Core, Neon, Tobii Pro Glasses 3 | 200° × 135° (binocular visual field) | 21 206 deg² |

## 2. Latency

The expected pupil is delayed by `delay` (default 0.5 s), the pupil's response latency. It is always applied, and
fitted per participant by the [calibration fit](calibration-fit.md).

## 3. Dynamics (optional)

One switch, `dynamics`, turns on everything in this section: the attack/release filter, its constriction stages and
the transient (4). The delay is applied either way.

With `dynamics` on, a one-pole filter with different time constants for the two directions:

\[
y_n = \alpha\, y_{n-1} + (1 - \alpha)\, x_n, \qquad \alpha = e^{-1/(f_s \tau)}
\]

\[
\tau = \begin{cases}\tau_\text{attack} & \text{if } x_n > y_{n-1} \text{ (dilation)} \\ \tau_\text{release} & \text{otherwise (constriction)}\end{cases}
\]

Dilation is slow (`attack`, default 6 s) and constriction fast (`release`, default 0.5 s). The filter acts on the
expected diameter after the formula and starts from the first value.

A one-pole constriction starts at full speed, while the pupil's starts gradually. With `constriction_stages` = 2 a
second stage with the same time constant `release` acts while the pupil constricts (it follows the first stage
directly while that rises), so the constriction is S-shaped, like that of a critically damped second-order system,
and dilation is unchanged. `release` is then the time constant of each stage.

## 4. Transient (with the dynamics)

After a brightening step the pupil constricts beyond its new steady state and then re-dilates towards it within a
few seconds ("pupillary escape"). On the seven Varjo calibration recordings the model without it misses a dip of
0.43 mm on average 1 s after a brightening step, which recovers with a time constant of 1–2 s. With `dynamics` on
and `transient` above 0, the expected pupil is reduced by

\[
T(t) = \text{transient} \cdot \frac{h}{h + h_0}, \qquad h = \max\big(0,\; \log_{10} L - \mathrm{LP}_{\tau_\text{escape}}(\log_{10} L)\big)
\]

where \(\mathrm{LP}_\tau\) is a one-pole low-pass with time constant `escape`: \(h\) is the increase of log luminance
over its recent level, jumping at a brightening step and decaying with `escape`. Darkening gives no transient. The
response saturates with the step size (\(h_0\) = 0.2 log units, fixed: the measured re-dilation grew from 0.25 mm for a
0.1 log unit step to 0.52 mm for a 1 log unit step), so `transient` is the largest transient constriction in mm. It
has the same latency as the rest and passes through as many one-pole low-passes with the constriction time constant
`release` as there are constriction stages.

## Display range

For display devices the expected pupil at \(L_\text{min}\) and \(L_\text{max}\) is shown as the dashed black and
white point lines: the range of pupil sizes the display can explain for this participant.

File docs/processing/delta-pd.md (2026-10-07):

# ΔPD and alignment

`pipeline.run`. Comparing the measured pupil with the expected one.

## Offset

The model predicts the pupil of an average observer, so the measured pupil is shifted onto it. `alignment` sets how
the offset is chosen:

| Mode | Offset | Use |
|---|---|---|
| `recording` | median of expected − measured over the whole recording | default, as in 1.x; ΔPD is centred on zero |
| `baseline` | the same median, over the events named in `baseline_events` (default "Riposo, Rest, Baseline") | ΔPD relative to rest phases; falls back to the whole recording with a warning if none are found |
| `fixed` | `pupil_offset` | the value fitted on the participant's calibration sequence, applied unchanged |
| `none` | 0 | absolute comparison |

Only valid samples (outside long gaps) enter the median.

## ΔPD

\[
\Delta PD = PD_\text{measured} + \text{offset} - PD_\text{expected}
\]

averaged over consecutive windows of `cw_window` (0.2 s), ignoring missing samples, then smoothed with a first-order
Savitzky–Golay filter over `cw_smoothing` windows on each side (1: three windows). Windows without valid samples stay
empty.

## Statistics

| Value | Meaning |
|---|---|
| ΔPD RMS | root mean square of ΔPD about zero: how far the pupil strays from the model overall |
| ΔPD SD | standard deviation of ΔPD: its spread around its own mean |
| ΔPD in SD units | ΔPD / SD, exported next to ΔPD in mm |
| Light left in ΔPD | how much of ΔPD the luminance still explains: the slope of ΔPD on log₁₀ luminance (mm per tenfold luminance) and the R² of ΔPD on log₁₀ luminance and its recent change, without the windows within 0.5 s of a luminance step (there the smoothed measured pupil and the expected one differ even for a perfect model). Shown in the summary; a warning above R² 0.1 |

The light left in ΔPD is the first check of a result: if the model removed the light, ΔPD does not follow the
luminance, and both figures are near 0. A large value means ΔPD changes where the light changes may not be workload.
It cannot tell model error from a task that itself follows the light (a bright task screen and a dark rest screen):
there, judge it on a recording, or a part, where the light varies and the task does not.

Absolute ΔPD in mm depends on the light sensitivity, the display photometry and the offset. Reporting changes relative to a baseline,
or in SD units, compares better across participants; Eckert et al. (2022) reach the same conclusion for
PLR-corrected pupil sizes.

## Events

For each event, the mean ΔPD inside it (in mm and SD units) is written to the events CSV. Events come from the
`event_log` CSV and, for the Neon and the Glasses 3, from the recording's own events.

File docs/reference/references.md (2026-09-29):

# References

## This tool

The methods implemented here:

- Pignoni, G., Komandur, S., & Volden, F. (2021). Accounting for effects of variation in luminance in pupillometry
  for field measurements of cognitive workload. *IEEE Sensors Journal*.
  [doi:10.1109/JSEN.2020.3038291](https://doi.org/10.1109/JSEN.2020.3038291). The lux sensor method (eq. 5–8) used
  for the glasses (Pupil Core, Neon, Glasses 3).
- Pignoni, G., Grandi, F., & Peruzzini, M. *Toward Reliable Pupillometry in Extended Reality Environments: A
  Video-Based Pipeline for Isolating Cognitive Workload from Pupil Data*. **Manuscript in preparation, not yet
  published**; the method may change before publication. Display photometric calibration, two-area luminance and the
  calibration sequence used for the Varjo XR-4. Pages that refer to "the Varjo manuscript" mean this text.

Related publications using the tool and its lux sensor:

- Pignoni, G., & Komandur, S. (2019). Development of a quantitative evaluation tool of cognitive workload in field
  studies through eye tracking. *Lecture Notes in Computer Science*, 11571.
  [doi:10.1007/978-3-030-22507-0_9](https://doi.org/10.1007/978-3-030-22507-0_9)
- Pignoni, G., Hareide, O. S., Komandur, S., & Volden, F. (2019). Trial application of pupillometry for a maritime
  usability study in field conditions. *Necesse*, 4.
  [NTNU Open](https://ntnuopen.ntnu.no/ntnu-xmlui/handle/11250/2633600)
- Streilein, T., Komandur, S., Pignoni, G., Volden, F., Lunde, P., & Mjelde, F. V. (2020). Maritime navigation:
  characterizing collaboration in a high-speed craft navigation activity. *Communications in Computer and Information
  Science*, 1224. [PDF](https://fhs.brage.unit.no/fhs-xmlui/bitstream/handle/11250/2786638/HCI_International_2020_Tim-3.pdf?sequence=1&isAllowed=y)
- Pignoni, G., & Komandur, S. (2022). Practical challenges in using eye trackers in the field. In *Human-Automation
  Interaction: Mobile Computing* (pp. 653–662). Springer.
  [doi:10.1007/978-3-031-10788-7_37](https://doi.org/10.1007/978-3-031-10788-7_37)

## Models

- Watson, A. B., & Yellott, J. I. (2012). A unified formula for light-adapted pupil size. *Journal of Vision*,
  12(10):12.
- Stanley, P. A., & Davies, A. K. (1995). The effect of field of view size on steady-state pupil diameter.
  *Ophthalmic & Physiological Optics*, 15(6), 601–603.

## Related work

- Eckert, M., Robotham, T., Habets, E. A. P., & Rummukainen, O. S. (2022). Pupillary light reflex correction for
  robust pupillometry in virtual reality. *Proc. ACM Comput. Graph. Interact. Tech.*, 5(2), Article 18.
  [doi:10.1145/3530798](https://doi.org/10.1145/3530798). Per-participant mapping functions from calibration
  sequences (6 s steps in pseudo-random order proved most robust) and luminance from a weighted average of the
  fixation area and the background.

## Data formats

- Varjo Base eye tracking recorder output (checked against an April 2026 export).
- Pupil Labs, Pupil Core raw data exporter (Pupil Player).
- Pupil Labs, [Neon recording format](https://docs.pupil-labs.com/neon/data-collection/data-format/) and
  [pl-neon-recording](https://github.com/pupil-labs/pl-neon-recording).

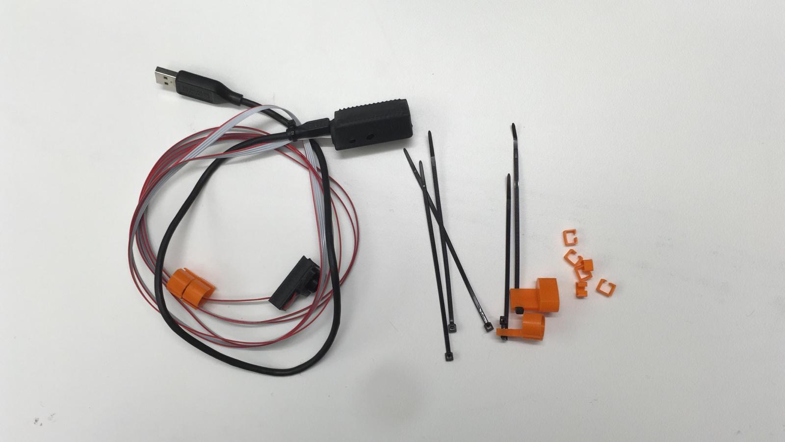
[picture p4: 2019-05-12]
Lux Sensor/Mount Hardware/A complete kit.jpg

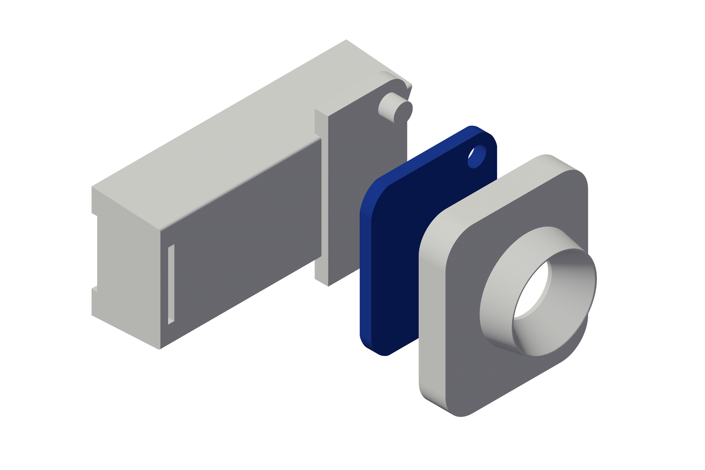
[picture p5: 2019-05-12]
Lux Sensor/Mount Hardware/the sensor housing.png

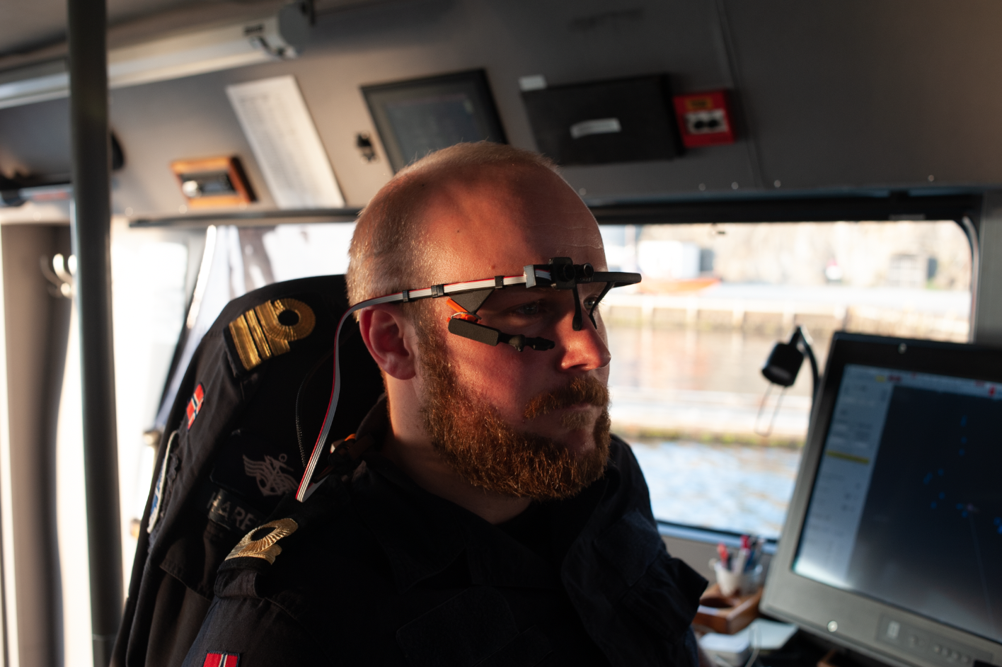
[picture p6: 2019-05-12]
Lux Sensor/Mount Hardware/A complete eyetracker.png

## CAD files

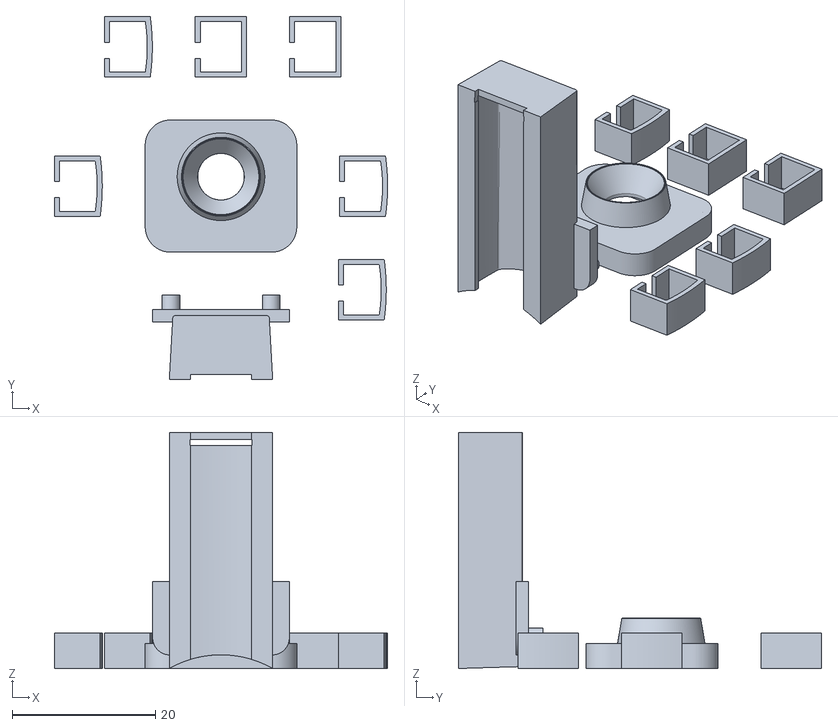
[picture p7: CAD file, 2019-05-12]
Lux Sensor/Mount Hardware/Adafruit Pupil lumiance sensor kit.stl
46.6 x 50.8 x 33.0

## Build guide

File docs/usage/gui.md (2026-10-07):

# Desktop app

Start it with `cwtool-gui`, optionally followed by a recording folder, or with `python -m cwtool.gui`.

## Layout

The window has the controls on the left, the plots on the right, and the video preview under the controls.

| Area | Contents |
|---|---|
| Rail (far left) | Four tabs: **Data**, **Params**, **Calibrate**, **Export** (Ctrl+1 to Ctrl+4). A red dot under a tab's name says it needs attention, for example **Data** when a glasses recording has no lux readings |
| Tab page | **Data**: the recording, the lux log (glasses), the scene video and its analysis settings, the sensor data. **Params**: the parameters, in pills (below). **Calibrate**: numbered steps. **Export**: the export range and the Export button |
| Video preview | Under the page, 16:9, following the cursor. **Values** shows the colours and luminance measured at the cursor, **Pop out** moves it to a window of its own, **Hide** (or **P**) gives its room back to the page. Drag the divider above it to resize |
| Status strip | One line over the plots: ΔPD RMS and SD, the light left in ΔPD, the expected pupil at the display's black and white points (display devices) or where the luminance comes from (with the lux sensor: its median luminance × the median video ratio and its 10th–90th percentile range), the pupil scale and offset applied, sampling rates and the share of the recording in gaps. A red **⚠ N warnings** button on its right opens the list |
| Plots | Measured vs expected pupil, luminance, the video ratio (lux sensor with the video only) and ΔPD, sharing the time axis, with the imported sensor signals under them. They use the whole width of the window |

The last tab, pill, preview state and sizes are remembered between sessions.

### Params: pills

| Pill | Holds |
|---|---|
| **Participant** | age, eyes, and the **Dynamics** drop-down (latency, time constants, transient: fitted per participant) |
| **Light** | only what applies to the device: display photometry and the participant's light response (Varjo), or the lux sensor and the scene camera without a lux log (glasses) |
| **Signal** | the pupil signal (scale, alignment, offset, time lag, gaps, artefacts) and ΔPD (window, smoothing) |

A dot after a pill's name means something in it differs from the defaults. **Restore this group's defaults** (under
the pills, with a confirmation) puts the open pill's settings back. **Load…**, **Save** and **Save as…** at the top
of the tab are the participant's parameter file.

## Menus

**File**

- **Open recording…**: choose a recording folder. The device is detected automatically.
- **Choose lux folder…**: one folder with the lux sensor logs for all glasses recordings, so the logs need not be
  copied into each. Its subfolders are searched (one per day is fine) and only the logs that overlap the recording are
  read. It is remembered between sessions, shown in the Recording box, and used instead of any logs inside the
  recording. If it holds no readings for a recording, a warning says so (check the folder and the loggers' clocks).
- **Use the recording's own lux logs**: forget the folder and go back to the recording folder or its `lux` subfolder.
- **Load parameters… / Save parameters / Save parameters as…**: the participant's parameter file (JSON), without
  the display photometry. Files written by version 1.x are converted when loaded.
- **Load display photometry… / Save display photometry…**: the headset's nominal Lmin, Lmax and gamma. The last
  file used with a device is loaded automatically with its recordings; the window title shows which one is in use.
- **Import sensor data…**: the Shimmer and EmotiBit files of a [sensor logger](logger.md) session, shown under ΔPD
  and exported with the results (see [Sensor data](#sensor-data-optional)).
- **Export results…**: one package into a folder of your choice (default `cwtool_export` inside the recording): the
  results CSVs, the sensor files, the parameters used, a manifest and a PDF plot, all trimmed to the
  [export range](#export-range).

**View**

- **Reset view** (Ctrl+0): show all the data on the plots again.
- **Show video preview** (P): show or hide the preview under the tab pages.
- **Data tab**, **Params tab**, **Calibrate tab**, **Export tab** (Ctrl+1 to Ctrl+4).

## Sensor data (optional)

Files from the [sensor logger](logger.md), the Shimmer's ECG and the EmotiBit's EDA, PPG and motion, can be put next
to the pupil data. They are not used by the analysis; they let you see heart and skin responses against ΔPD, and
export everything for one participant as a single package.

- **Import…** (or **File → Import sensor data…**): choose a logger session folder. When a recording is opened, the
  logger's files in its own folder are imported automatically. Only the rows that overlap the recording are read. The
  recording must say when it started (its absolute time), as the sensor files are on the Unix clock.
- The list under the buttons holds every signal of every file (the Shimmer's channels, the EmotiBit's streams). The
  ticked ones are drawn, one plot each, under ΔPD on the same time axis, cursor and events; at first the ECG channel
  of the Shimmer and the EmotiBit's EDA and PPG. At most six at a time.
- Values are shown as the logger saved them: the Shimmer's are raw ADC counts, not millivolts.
- **Remove** forgets the sensor data. All the signals, not only the ticked ones, go into the export.

## Export range

What the export leaves out: the calibration sequence, a break, a test run before the participant started. The
analysis and the plots always use the whole recording (the model needs the history of the light); the range only
decides what is written by **Export results…**, for every file at once (results, lux, sensors, events).

- **Start at / End at**: leave out everything before or after a time. **Cursor** takes the time of the red cursor.
  Both are drawn on the plots as dashed lines you can drag.
- **Left out**: any number of segments in between, drawn as grey bands. **Leave out from cursor** adds 10 s at the
  cursor to adjust; **Leave out calibration** leaves out the calibration sequence while its overlay is shown. Drag a
  band by its body or edges on the pupil plot, or double-click a row (or **Edit…**) to type the times. Bands dragged
  over each other merge.
- Times are those of the plots' axis (`timestamp_relative` in the exports).
- The range is saved next to the recording (`cwtool_trim.json`) and comes back when it is opened again; clearing it
  removes the file. It is separate from the participant's parameter file, since it belongs to one recording.

ΔPD in SD units (`delta_pd_sd`) is normalised with the SD of what is kept, so a calibration with large swings does not
shrink the other values; see [Output files](../reference/outputs.md).

## Scene video

The video is analysed automatically when a recording is opened, unless a cached analysis made with the same
video, settings, frame timestamps and gaze exists. **Reanalyse video** (**Analyse video** before any analysis) runs
it again, for example after changing the video analysis settings; **Cancel**, shown while it runs, stops it.

**Video analysis settings** (drop-down under the buttons: gaze circle radius, scene circle, background, analysis
width) change what is measured in the video: after editing them, click **Reanalyse video**. The video preview
already draws the new circles, so sizes can be checked before re-running.

**Calibrate camera from lux** (glasses recordings with a lux log): measures the luminance that saturates a
fixed-exposure scene camera, for recordings of the same exposure without a lux log (see
[Luminance](../processing/luminance.md#calibrating-the-camera-from-a-lux-log)).

## Parameters

Parameters are in the pills of the **Params** tab, with the groups of [Parameters](../reference/parameters.md): Participant
(with Dynamics in a drop-down), Display photometry, Participant light response, Luminance from lux sensor, Scene camera
without lux log (these four under Light), Pupil signal and ΔPD (under Signal). The video analysis settings are in a
drop-down under the scene video buttons, in the **Data** tab. Every change re-runs the analysis from the cached video
pass, so the plots follow instantly.

Only the options that affect the loaded recording are shown (all of them before a recording is opened); hidden
options keep their values and are still saved in the parameter file:

| Recording | Hidden |
|---|---|
| Varjo | Lux sensor, Scene camera without lux log |
| Pupil Core / Neon / Glasses 3 with a lux log | Lmin, Lmax, Scene camera without lux log, scene circle radius |
| Pupil Core / Neon / Glasses 3 without a lux log | Lux sensor, Calibration sequence, scene circle radius; with camera exposure `auto` the camera full scale and exposure times, with `fixed` Lmin and Lmax |

The **Calibrate** tab depends on the device. A display device (Varjo) has three steps: the sequence, **Fit light
sensitivity** and **Fit latency and offset**. Glasses with a lux log have the sequence and one fit, **Fit sensitivity
and offset**, with a note that they have no display photometry (see below). Glasses without a lux log have no steps,
only a note saying what the sequence would need; their dynamics are set by hand in Params → Participant. Once a fit
is applied, its step shows the result under its title. The lux sensor group starts with a line saying which route the luminance takes (sensor ×
video ratio, or sensor only); the video preview shows the same product for the frame at the cursor, and the weights
of the gaze circle and the background.

## Plots

- The view fits the data when a recording opens and follows it while you change parameters. Drag with the left
  mouse button to pan and use the wheel to zoom; after that the view stays where you put it.
- **Reset view** (button in the top right corner of the plots, **View** menu, Ctrl+0, or a double-click on the
  plots) shows all the data again: the whole recording and the range of the measured, expected and ΔPD curves. The calibration overlay, events and reference
  lines never stretch it.
- Right-click for pyqtgraph's view menu (e.g. export an image).
- The dark orange bar marks the current video frame; its time is shown at its top. Click on either plot to move it, or drag it to
  scrub the video: the preview follows while dragging, skipping frames if decoding cannot keep up. **◀ Frame / Frame ▶**
  in the preview move it frame by frame.
- **Luminance** (second plot): the luminance the model uses, in cd/m². With a lux sensor the sensor's average is drawn
  dashed behind it, so the video's contribution is the difference between the two.
- **Video ratio** (third plot, lux sensor with the video): gaze-weighted over whole-frame relative luminance, the
  factor that turns the sensor's average into the luminance used. It follows where the gaze looks; on a uniform view
  it should stay near 1 on a uniform view, and a wide spread is a prompt to compare with *Distribute with the
  scene video* turned off (the summary line then warns): it helps when the sensor sees little of the changing
  screen and only adds noise on a uniform view.
- The dashed green lines are the expected pupil at the display's black and white points: the range the model can
  explain on that device.
- Events from the event log are shaded orange and labelled in the ΔPD plot.

## Calibration sequence

See [Participant calibration](calibration.md) for the procedure.

- **Load sequence… / Built-in**: the colour sequence to overlay: a built-in one (the presenter's full calibration, or the
  20-step staircase used before October 2026), a CSV, or a run file saved by
  the [calibration presenter](calibration-tool.md). A run file's onset times are on the presenting computer's clock,
  so they place the sequence in the recording (the start and the overlay are set; a run played for another recording
  is reported as outside it).
- **Find in recording**: locates the sequence in the analysed video and adapts its step length.
- **Show sequence overlay**: shades each step in its colour on the pupil plot; drag the grey line to move it.
- **Start**: the sequence start in seconds.
- **ΔPD RMS in sequence**: how well the model fits within the sequence, the value to minimise when calibrating
  by hand.
- **Fit light sensitivity** (step 2): the participant's light sensitivity and channel weights (optionally gamma and the display's black level, *Also fit the black level*), with a
  result window showing each step's steady-state pupil against the model.
- **Fit latency and offset** (step 3): the participant's timing and dynamics (neither the pupil scale nor the offset is fitted: set
  *Pupil scale correction* and *Pupil offset* by hand), optionally with the
  transient constriction after brightening (pupillary escape). Its result shows two errors: the **fit error**, what
  the fit minimises (measured − expected in the sequence, without an offset), and the ΔPD RMS in the sequence with
  the current alignment (with alignment 'recording', after the whole recording's median offset).
- **Also fit the fixation weight** (glasses with a lux log): adds the gaze circle's weight to the fit below; it needs a
  scene where the gaze area and the background differ.
- **Fit sensitivity and offset** (glasses with a lux log): the participant's light sensitivity and the pupil offset by
  least squares on ΔPD over the sequence, with the luminance the analysis builds from the sensor (and the video). The
  result window gives the RMS before and after, the sensitivity with its interval, the correlation and warnings;
  Apply also sets the alignment to `fixed` (see [Calibration fit](../processing/calibration-fit.md#glasses-with-a-lux-sensor)).
- **Dynamics** (Params → Participant, drop-down): the latency, always applied, and one switch for the rest: dilation and constriction time
  constants, constriction stages, transient and escape τ (greyed out while the switch is off).

## Video preview

Shows the scene frame matched to the cursor time (by recorded frame timestamps where the device provides them),
the scene circle used as background on Varjo videos (green), the gaze circle (orange), and, with **Values**, the mean
colour and luminance measured in each. **◀ Frame / Frame ▶** step through frames. It sits under the tab pages; **Pop
out** puts it in its own window to see the frame larger and **Dock back** (or closing that window) returns it.

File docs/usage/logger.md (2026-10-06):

# Sensor logger

A desktop app that records the lux sensor, a Shimmer (ECG and other signals) and an EmotiBit side by side, on the
computer's clock, together with the phases of the experiment. It replaces running `tools/lux_logger.py` and
`tools/event_logger.py` separately (see [Lux and event loggers](tools.md), which still work).

```bash
pip install -e ".[logger]"
cwtool-logger                 # or: python -m cwtool.logger
```

!!! warning "On macOS, start it from Terminal"
    The Shimmer is reached through macOS's Bluetooth, and macOS ends any program that uses Bluetooth unless the app
    that started it has been allowed to. Terminal asks the first time (allow it); the Claude app, and some editors'
    built-in terminals, are not allowed. The logger checks first, and adding a Shimmer from such an app fails with
    "This app may not use Bluetooth".

## Recording

1. **Add the sensors** with the *+ Lux*, *+ Shimmer*, *+ EmotiBit* buttons (see below). Each sensor gets a live plot
   as soon as it is connected, so the signals can be checked before recording; nothing is saved yet. Choose the signal
   shown with the drop-down above each plot.
2. **Pick the folder** for the recordings (remembered between sessions) and press the green **Start recording**
   button. It turns red (**Stop recording**) with the elapsed time beside it.
3. **Mark the phases** of the experiment, if any (see [Events](#events)).
4. Press **Stop recording**. The folder is shown in the status bar.

Sensors can be added or removed while recording; one added during a recording starts its own file at that moment.
The table lists each sensor's status (*ok*, *waiting for data*, *silent* with the seconds since its last sample, or
the error that stopped it), its row count and the time since the last row.

### What the plots show

The time axis is the last 30 s. The value axis follows the data: the span of the signal with a margin, ignoring the
outermost 0.5 % so one spike does not flatten it, and at least 1 % of the signal's level so noise on a flat signal is
not magnified.

## The sensors

### Lux sensor

The [TSL2591 logger](../hardware/lux-sensor.md) on a USB port. *+ Lux* finds the board by its name (Adafruit, Arduino,
CH340 "USB2.0-Serial"); choose the port by hand if several are connected. About 10 readings per second.

### Shimmer

A Shimmer3 running the LogAndStream firmware (the one Consensys uses), streaming over Bluetooth. The sensors enabled
on the device in Consensys are the ones logged, as the **raw values the device sends** (ADC counts); converting to
mV or µS is done in the analysis. Typical sampling rate 51.2 Hz.

- **Windows and Linux:** pair the Shimmer in the system's Bluetooth settings, then choose its serial port in the add
  dialog (`COM5`, `/dev/rfcomm0`, ...).
- **macOS:** pair it in *System Settings → Bluetooth*. The add dialog lists the paired Shimmers by name and address
  (`Shimmer3-873A  (Bluetooth 00-06-66-...)`) and connects to them directly, because the `/dev/cu.Shimmer...` port that
  macOS creates often stays silent. The first attempt can fail and be repeated automatically; connecting takes up to
  half a minute. See the warning above about starting from Terminal.

When connecting, the logger sets the Shimmer's real-time clock to the computer's time (tick the box in the add dialog
off to skip it), as Consensys does, and saves the offset it measured in `session.json` (`real-time clock`). This does
**not** change the logger's files: the streamed samples are stamped by another clock (ticks since power-on, mapped onto
the computer's time as described under [Clocks](#clocks)). It makes the unit's own SD card recordings agree with the
computer, and clears the blue/green "clock not set" light. The clock is lost when the unit is switched off, and it does
not correct the drift of the unit's oscillator.

Switch the Shimmer on and wait for its slow blue blink (standby) before connecting; only one computer can be
connected to it at a time, so close Consensys first. Its status lights:

| Light | Pattern | Meaning |
|---|---|---|
| upper, blue | 0.1 s on, 2 s off | standby, waiting for a connection |
| upper, blue | solid | connected |
| upper, blue | 1 s on, 1 s off | streaming |
| upper, blue / green | alternating, 0.1 s each | the unit's clock is not set (normal after switching on), or no configuration file on its SD card; streaming still works |
| lower | yellow solid, green solid | charging, full (docked) |
| lower | green, yellow, red, 0.1 s every 5 s | full, medium, low charge (undocked) |

A solid red lower light means the battery is critically low: a unit in that state may show the Bluetooth connection
but never answer. Charge it first.

### EmotiBit

The EmotiBit sends its data over Wi-Fi to the **EmotiBit Oscilloscope**, which can publish it as
[Lab Streaming Layer](https://labstreaminglayer.org) (LSL) streams; the logger reads those. So the Oscilloscope must be
running, connected to the device, with its **LSL output enabled**; the logger does not talk to the EmotiBit directly.

- The EmotiBit joins a **2.4 GHz** Wi-Fi network named in a `config.txt` on its SD card
  (`{"WifiCredentials": [{"ssid": "...", "password": "..."}]}`), or entered over USB serial with the `C` key. Without
  it the Oscilloscope cannot find the device. The computer must be on the same network (and subnet).
- The USB cable is for power, flashing and status messages only; sensor data does not travel over it.
- The Oscilloscope publishes one single-channel stream per signal (EDA, PPG_RED, ACC_X, HR, ...), all carrying the
  device ID (for example `MD-V7-0000188`) as their source. *+ EmotiBit* lists the devices found on the network (this
  takes a couple of seconds) and records all the streams of the one you choose.

## Events

The phases of the experiment are saved in `event_log.csv`, the file the analysis reads to shade and average ΔPD per
phase. They are only recorded while recording.

- **Manual:** type a name and press *Begin* (or Enter). The running phase, if any, ends at the same instant; *End*
  ends it without starting another.
- **Protocol:** *Load protocol…* reads a CSV with one `name,duration` per line (duration in seconds, blank = until
  you press *Next phase*; lines starting with `#` are comments), the same format as `tools/example_protocol.csv`.
  *Start protocol* begins the first phase; phases with a duration advance by themselves, the others wait for *Next
  phase*. The current phase and the time left are shown below the buttons.

Stopping the recording ends the running phase.

## What is saved

Each recording gets its own folder, named by the date and time it started:

```text
<recordings folder>/2026-10-06_15-30-00/
├── lux.csv
├── shimmer.csv
├── emotibit.csv
├── event_log.csv
└── session.json
```

One file per sensor, named after the sensor (a second Shimmer would be `shimmer_2.csv`), written while recording and
flushed every second, so a crash loses little. Every data file starts with a header and its first column is the
**Unix time in seconds** on the computer's clock, so the analysis cuts the span it needs from each file.

| File | Columns |
|---|---|
| `lux.csv` | `unix time (s)`, `lux` |
| `shimmer.csv` | `unix time (s)`, `device time (s)`, then one column per enabled channel (`accel_ln_x`, `gyro_mpu9150_x`, `exg_ads1292r_1_ch1_24bit`, ...), raw values |
| `emotibit.csv` | `unix time (s)`, `signal`, `value`: one row per sample, with the stream name (`EDA`, `PPG_RED`, ...) as the signal, so signals of different rates share the file |
| `event_log.csv` | `Event`, `Start Time`, `End Time`, `Duration (s)`, `Start (unix s)`, `End (unix s)`, as written by `tools/event_logger.py` |
| `session.json` | start and end, the computer's UTC offset, and for each sensor its file, kind, columns, settings (port, sampling rate, ...) and row count |

The main app can show the Shimmer and EmotiBit files under ΔPD and export them with the results, trimmed to what
you choose ([Sensor data](gui.md#sensor-data-optional)).

`lux.csv` is read by the analysis as it is: put it (the recording's folder) with the eye tracker's recording, or
point the *lux folder* setting at it ([Luminance](../processing/luminance.md#lux-sensor-devices)). The older hourly
`<month>_<day>_<hour>.csv` files remain supported.

### Clocks

All times are the Unix time of the computer running the logger. Run it on the computer that records the Pupil Core and
both share a clock; for the Neon, whose timestamps come from the phone, see
[clock synchronisation](../devices/pupil-neon.md#clocks).

- **Lux:** stamped when the line arrives over USB.
- **Shimmer:** its own clock is regular but drifts, and Bluetooth delivers samples in bursts. `device time (s)` is the
  device's clock (zero at the first sample) and `unix time (s)` maps it onto the computer's clock, using the smallest
  difference between the two over the last minute (the sample that arrived with the least delay), so the burst delay
  does not enter. Both columns are saved, so the mapping can be redone.
- **EmotiBit:** LSL's own clock synchronisation and de-jittering, then converted to Unix time. In a test the newest
  sample was about 0.35 s old when the logger received it; that is delivery delay, and whether the timestamps
  themselves are exact has not been measured.

These assumptions have not been checked against an external reference ([open issue 49](../OPEN_ISSUES.md)); the
check below measures them.

### Checking the clocks

A recorded session can be checked for the quality of its timestamps:

```bash
python -m cwtool.logger.clockcheck SESSION_FOLDER [--save]
```

It reports, for each file, the sampling rate and how much the time between samples varies (for the lux sensor, whose
lines are stamped when they arrive, this is its timestamp jitter); for the Shimmer, how fast its own clock runs against
the computer's (ppm) and how far the mapping wanders around a straight line; and the **offset between the Shimmer and
the EmotiBit**, from the movement both accelerometers feel.

To measure that offset, fix the Shimmer and the EmotiBit together (tape them to each other, or to a board), record
about a minute with both connected, and **knock the table sharply five or six times**, a few seconds apart, without
moving them otherwise. The check finds the lag that best matches the two accelerometers' movement; a positive value
means the EmotiBit's timestamps are late with respect to the Shimmer's. It says when the match is weak. Do it once per
setup (a long recording, a different Wi-Fi network) and keep the result with the study. `--save` writes
`clock_check.json` into the session folder.

## When something does not work

- **The window freezes.** If it stops responding for more than 2 s, the stack of every thread is written to
  `stall.log` in the recordings folder. Send it with a note of which sensors were connected.
- **A sensor says *silent*.** The device stopped sending: check its battery, its connection, and for the EmotiBit that
  the Oscilloscope is still connected and streaming.
- **Shimmer: no answer.** Not in standby (switch it off and on), still connected to Consensys or another computer, a
  flat battery (red light), or, on macOS, the program was not started from Terminal.
- **EmotiBit: not in the list.** The Oscilloscope does not see it (Wi-Fi settings, 2.4 GHz, same network), or its LSL
  output is off.
- **Disk errors** (for example a full disk) are shown in the status bar; the recording goes on, and the rows that could
  not be written are missing from the file.

## From Python

The window is a thin layer over classes that do not use Qt:

```python
from pathlib import Path
from cwtool.logger import Logger
from cwtool.logger.sources import LuxSerialSource, ShimmerSource, LslSource

log = Logger()
log.add(LuxSerialSource())                        # connects, then streams into live buffers
log.add(LslSource("MD-V7-0000188", name="emotibit"))
session = log.start_recording(Path("recordings"))
log.mark("Baseline")                              # begin an event
...
log.stop_recording()                              # returns the session folder
log.shutdown()
```

A new sensor is a `Source` subclass (`cwtool/logger/base.py`): `open()` connects and sets `columns`, `run(emit,
stopped)` calls `emit([(unix_time, value, ...), ...])` until `stopped` is set.

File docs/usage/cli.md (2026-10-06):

# Command line

```text
cwtool RECORDING [--device {pupil_core,pupil_neon,tobii_g3,varjo}] [--params FILE] [--display FILE]
                 [--lux FOLDER] [--sensors FOLDER] [--start S] [--end S] [--exclude FROM TO]
                 [--out FOLDER] [--reanalyse] [--workers N] [--plot]
```

| Option | Meaning |
|---|---|
| `RECORDING` | recording folder |
| `--device` | skip auto-detection |
| `--params` | participant parameter file (JSON) saved by the app; defaults otherwise |
| `--display` | display photometry file (JSON) saved by the app (Varjo); participant files do not hold Lmin, Lmax and gamma, so without it the defaults are used |
| `--lux` | folder with lux sensor logs (glasses), searched with its subfolders; default: the recording folder or its `lux` subfolder |
| `--sensors` | [sensor logger](logger.md) session folder (Shimmer, EmotiBit) to add to the export, trimmed like the rest; default: any logger files in the recording folder |
| `--start`, `--end` | leave out everything before or after this time, in seconds on the exports' `timestamp_relative` axis |
| `--exclude FROM TO` | leave out FROM to TO seconds, for example a calibration; repeat for several segments |
| `--out` | export folder; default `RECORDING/cwtool_export` |
| `--reanalyse` | ignore the cached video analysis |
| `--workers` | parallel video chunks; default one per CPU core |
| `--plot` | also save a PDF plot (needs the `plot` extra) |

The command prints the device, the ΔPD RMS and SD, and any warnings, then writes the
[output files](../reference/outputs.md). The analysis always runs on the whole recording; `--start`, `--end` and
`--exclude` only trim what is written. Without them, the export range saved by the app next to the recording
(`cwtool_trim.json`) is used.

## Batch processing

A shell loop over participants, each with their own parameter file:

```bash
for p in P01 P02 P03; do
  for rec in data/$p/*/; do
    cwtool "$rec" --params "params/$p.json" --display params/varjo_xr4.json --out "results/$p/$(basename "$rec")"
  done
done
```

## From Python

Everything the app does is available as functions:

```python
from pathlib import Path
from cwtool import devices, pipeline
from cwtool.params import DisplayPhotometry, Parameters, VideoSettings
from cwtool.video import VideoResult, analyse_video

rec = devices.load(Path("data/P01/rec1"))              # auto-detects the device
params = Parameters.load("params/P01.json", rec.profile)
params = DisplayPhotometry.load("params/varjo_xr4.json").apply(params)   # display devices
settings = VideoSettings().for_recording(rec)

video = VideoResult.load_cached(rec.folder, settings, rec.scene_video, rec.scene_frame_times, rec.gaze)
if video is None:
    video = analyse_video(rec.scene_video, rec.time, rec.gaze, settings, frame_times=rec.scene_frame_times)
    video.save(rec.folder, settings, rec.scene_video, rec.scene_frame_times, rec.gaze)

result = pipeline.run(rec, video, params)
print(result.cw_rms, result.warnings)
pipeline.export(result, rec, params, Path("out"))

# one package for a participant, trimmed, with the sensor logger's files
from cwtool import sensors
from cwtool.trim import Trim
found = sensors.load_sensors(Path("session"), rec.epoch_start + rec.time[0], rec.time[-1] - rec.time[0])
pipeline.export(result, rec, params, Path("package"), sensors=found,
                trim=Trim(start=60.0, exclude=[(310.0, 600.0)]))   # leave out the first minute and a calibration
```

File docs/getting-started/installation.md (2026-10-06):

# Installation

The tool needs Python 3.10 or newer and runs on Windows, macOS and Linux.

## From the repository

```bash
git clone -b master_v2.0 https://github.com/pignoniG/cognitive_analysis_tool.git
cd cognitive_analysis_tool
python -m venv .venv
source .venv/bin/activate          # Windows: .venv\Scripts\activate
pip install -e ".[gui]"
```

This installs two commands: `cwtool-gui` (desktop app) and `cwtool` (command line). The `logger` extra adds
`cwtool-logger`, the [sensor logger](../usage/logger.md).

## Optional extras

| Extra | Installs | Needed for |
|---|---|---|
| `gui` | PySide6, pyqtgraph, matplotlib | the desktop app |
| `plot` | matplotlib | `cwtool --plot` (PDF plots from the command line) |
| `logger` | pyserial, pyshimmer, pylsl, PySide6, pyqtgraph (and the macOS Bluetooth bindings on a Mac) | the [sensor logger](../usage/logger.md) and `tools/lux_logger.py` |
| `dev` | pytest | running the tests |

Combine them as needed, e.g. `pip install -e ".[gui,logger,dev]"`.

## Core dependencies

Installed automatically: NumPy, SciPy, OpenCV (`opencv-python`), PyAV (`av`, fast threaded video decoding; the tool
falls back to OpenCV when it is missing) and msgpack (Pupil Core camera intrinsics).

## Checking the installation

```bash
cwtool --help
pytest            # with the dev extra: all tests should pass
```

!!! tip "Linux without a desktop"
    The Qt app needs the system's OpenGL/EGL libraries. On a minimal Debian/Ubuntu install:
    `sudo apt install libegl1 libgl1`. The command line tool does not need them.

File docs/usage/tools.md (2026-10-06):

# Lux and event logger scripts

Two standalone scripts in `tools/` record data alongside the eye tracker. The
[sensor logger](logger.md) does the same and more in one window (lux sensor, Shimmer, EmotiBit and events, one
folder per recording); these scripts remain for command-line use and for the 1.x file format.

## Lux logger

Logs the [TSL2591 lux sensor](../hardware/lux-sensor.md) when its microcontroller is connected to a computer over
USB, instead of logging to the board's SD card.

```bash
pip install -e ".[logger]"
python tools/lux_logger.py OUTPUT_FOLDER [--port PORT] [--baud 250000]
```

Without `--port`, the first USB serial device that looks like one of the supported boards (Adafruit, Arduino,
CH340 "USB2.0-Serial") is used; if none is found, the available ports are listed. Stop with Ctrl+C.

Readings (about 10 per second) are appended to one CSV per hour, named `<month>_<day>_<hour>.csv` in local time,
with rows

```text
unix time (ms), day, hour, minute, lux
```

the same format as the SD card logger and version 1.x. The analysis reads only the first column (time) and the
fifth (lux).

!!! tip "Use the same computer as the eye tracker"
    Logging on the computer that records the Pupil Core puts both on the same clock. The SD card logger's
    real-time clock drifts by seconds per day and ignores time zones; compensate with the **time lag** parameter.
    For the Neon, whose timestamps come from the Companion phone, see
    [clock synchronisation](../devices/pupil-neon.md#clocks).

## Event logger

Times the phases of an experiment and writes the `event_log` CSV the analysis reads, so ΔPD is averaged per phase
and the phases are shaded on the plots.

```bash
python tools/event_logger.py PROTOCOL.csv [--out FOLDER]
```

The protocol file has one `name,duration` line per phase (seconds). A blank duration means the phase lasts until
you press Enter; lines starting with `#` are comments. `tools/example_protocol.csv` is the protocol of the
February 2026 Varjo pilot, a master's thesis that tested the system in a flight simulator:

```text
# name,duration in seconds (blank = press Enter to end the phase)
Riposo,60
Briefing,
CountB_7,
Riposo,30
...
```

Start the logger with the recording, press Enter to begin, and follow the prompts. The log is saved as
`<date>_event_log.csv` with columns `Event, Start Time, End Time, Duration (s), Start (unix s), End (unix s)`. Times are
ISO 8601 with the UTC offset and also Unix time, so the file reads the same on any computer. Copy it into the
recording folder.

Each phase starts at its own logged time, so pauses between phases are kept. The reader takes the Unix start when
present, else the ISO time. Logs from the older logger have ISO times without a zone: for Varjo recordings they are
read in the zone of the computer that recorded (from Varjo Base's file name, which is in local time), for Glasses 3
recordings in the recording unit's zone (`recording.g3`), for the Pupil devices in the zone of the computer running the
analysis.

!!! note "Neon and Glasses 3 events"
    Events marked in the Neon Companion app or in Pupil Cloud, and Glasses 3 events (`eventdata.gz`), are read
    directly from the recording; see [Pupil Neon](../devices/pupil-neon.md#events) and
    [Tobii Pro Glasses 3](../devices/tobii-g3.md). An `event_log` CSV in the folder is read as well.

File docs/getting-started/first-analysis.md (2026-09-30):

# First analysis

## 1. Prepare the recording folder

Each device has its own layout; the tool detects it from the files present.

- **Varjo XR-4:** the folder written by Varjo Base, with `varjo_gaze_output_*.csv` and `varjo_capture_*.mp4`.
- **Pupil Core:** the recording folder after exporting it in Pupil Player (it must contain `exports/<n>/`).
- **Pupil Neon** (experimental): a recording folder from a Pupil Cloud "Timeseries Data + Scene Video" download, or
  a native recording folder.
- **Tobii Pro Glasses 3** (experimental): the recording folder from the SD card, with `recording.g3` and
  `gazedata.gz`.

For the glasses (Pupil Core, Neon, Glasses 3), put the lux sensor logs (`<month>_<day>_<hour>.csv`) in the recording folder or a `lux`
subfolder, or point the app (**File → Choose lux folder…**) or `cwtool --lux` at the one folder where you keep them all:
it is remembered and needs no copying into each recording. Optionally add an `event_log` CSV from the
[event logger](../usage/tools.md#event-logger) to label the phases of the experiment.

## 2. Open it

```bash
cwtool-gui path/to/recording
```

or start `cwtool-gui` and use **File → Open recording…**. The recording panel shows the detected device, the
number of samples and, for the glasses, how many lux readings were found.

## 3. Analyse the scene video

The first time, the scene video is analysed in the background (a progress bar shows the video pass). The result
is cached next to the recording (`cwtool_video.csv`), so opening the recording again is instant. A 4-minute 4K
Varjo capture takes under a minute on a 4-core laptop.

## 4. Read the plots

- **Top:** measured pupil (black, grey = lightly smoothed) and expected pupil for the estimated luminance (green).
- **Bottom:** ΔPD (red), measured minus expected. Positive values mean a pupil larger than light alone explains.
- Shaded orange regions are events from the event log; click on either plot to move the video preview to that
  moment.

Every parameter change in the side panel updates the plots immediately.

## 5. Calibrate and save the participant's parameters

For Varjo recordings, enter the display photometry once, then fit the participant's light sensitivity and pupil
response on the calibration sequence (see [Participant calibration](../usage/calibration.md)) and
**File → Save parameters**.
Load the same file for that participant's other recordings.

## 6. Export

**File → Export results…** writes the pupil, ΔPD and per-event CSVs plus the parameters used
(see [Output files](../reference/outputs.md)).

The same analysis without the GUI:

```bash
cwtool path/to/recording --params participant.json --plot
```

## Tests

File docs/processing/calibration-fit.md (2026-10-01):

# Calibration fit

`cwtool/photometry.py`, `cwtool/fit.py` and `cwtool/calibration.py`. Estimates a participant's parameters from
their calibration sequence, given the display photometry. For the procedure, see
[Participant calibration](../usage/calibration.md).

## Locating the sequence

`calibration.locate` works on the video pass's gaze circle colour:

1. **Change points:** frames where any channel jumps by more than 8 code values, at least 0.3 s apart.
2. **Step length:** if the sequence's steps are all the same length, the median interval between change points
   gives the recording's step length, and a rescaled copy of the sequence is tried as well.
3. **Scoring:** every change point, aligned with every step start, is a candidate start. A candidate must lie within
   the recording, give or take its first and last step (which may have begun before the recording or been cut
   short). Within the candidate window the sequence's colours and the measured ones are compared in linear light,
   skipping the first half second of each step (the video changes a frame late). Only times with analysed video are
   compared: the video is analysed at valid gaze samples, so tracking gaps have no colour, and at least half of the
   window must have one. One gain per channel is fitted by least squares, because recorded levels are below nominal
   (on the Varjo sample grey 255 records as 253, red 255 as 231). The score is the relative RMS error.

The best candidate gives the start and, if rescaled, the new step timing.

## Light sensitivity

`photometry.fit_light_response`.

**What can be determined.** Watson & Yellott depend on luminance only through the product luminance × field area, so
scaling Lmin and Lmax together is indistinguishable from a participant whose pupil is more or less sensitive to
light. With the pupil scale also unknown (Varjo), one sequence cannot separate the display's brightness from the
participant's sensitivity. The display photometry is therefore taken as given (the user's nominal values), and one
**light sensitivity** factor \(s\) per participant multiplies the luminance entering the model:

\[
PD = WY(s \cdot L)
\]

Any error of the display photometry common to all participants is absorbed by \(s\).

**Level per step.** After the current latency, the level of each step is the mean of the lightly smoothed pupil over
its last 30 %. It is not extrapolated: on the seven Varjo calibration recordings the apparent trend at the end of a
step was as often a constriction as a dilation after brightening, i.e. mostly the pupil's own fluctuation, and
extrapolating it moved levels by 0.34 mm (median) and silently dropped a quarter of the steps
([open issue 40](../OPEN_ISSUES.md)). The one trend the physiology predicts is slow dilation after a darker step, which
can outlast a step: a step still dilating by more than 0.1 mm over its end after a darker one is flagged, its level
is short of the steady state, and half of that trend is added to its uncertainty. Each step's colour is its mean weighted gaze/background colour in the
video (after the first 0.5 s), so the fit sees the same, below-nominal levels as the analysis.

**Fit.** With the step luminances \(L_s\) from the display photometry and channel weights, the model is mapped onto
the measured steady states,

\[
A_s \approx WY(s \cdot L_s(g_R, g_G, g_B, \gamma, L_\text{min})) \; (+\, d)
\]

by weighted least squares (weights from each step's uncertainty, with a 0.1 mm floor for pupil fluctuations and model
error) over \(\log s\) and the log channel weights, and optionally \(\gamma\), \(\log L_\text{min}\) (white held at its nominal value) and an offset \(d\) (`fit_offset`, off by default; then \(b = -d\)). Residuals are in measured millimetres, at the pupil scale set by hand (`pupil_correction`): the scale is not fitted, because the sequence does not determine it (it trades off with the sensitivity and the black point, [open issues 1 and 36](../OPEN_ISSUES.md)). Weak priors keep poorly determined values near sensible ones: log weights around 0 (SD 1.5; wide, because
the pupil's colour weighting departs strongly from photopic luminance, blue in particular), \(\gamma\) around
2.2 (SD 0.2). The sensitivity has no prior, only its range (0.001–1000): a prior centred
on \(s = 1\) would mean "the display photometry is right", so it would pull the fit differently for different
datasheet values and break the exact trade-off between the two ([open issue 42](../OPEN_ISSUES.md)). Because the pupil
curve is S-shaped in log luminance, the fit starts from five sensitivities (0.03 to 30) and keeps the best. The weights are reported normalised to a mean of 1.

**Black level.** With *Also fit the black level* \(L_\text{min}\) is fitted within 0.0001–10 cd/m² while \(L_\text{max}\) stays at its nominal value; only \(s L_\text{min}\) and \(s L_\text{max}\) are determined, so holding the white fixes the scale of the pair. The notes report the contrast it implies against the nominal one. On the Varjo sample (8 s steps, black steps at 4.4 mm) it gives 0.21 cd/m² (481:1 against the datasheet's 10000:1), because the steps are too short to dark-adapt; with the nominal 0.01 the RMS is 0.76 mm instead of 0.66 (photopic weights).

**Sanity checks** (`luminance.display_notes`, also shown with every analysis): Lmax more than 10 % above the device's claimed peak luminance (Varjo: 200 cd/m²; it may be lower, since brightness is adjustable), Lmin not below Lmax, and a contrast below 100:1 are flagged ([open issue 48](../OPEN_ISSUES.md)).

**Uncertainty and warnings.** An approximate 95 % interval of \(s\) comes from the curvature at the solution. Notes
flag a wide interval (factor above 4), values at their limits, steps still dilating at their end, and skipped
steps.

**Synthetic check** (`tests/test_photometry.py`): a participant with sensitivity 3 and channel weights 1.5, 0.7, 0.8
on the 20-step staircase with 10 s steps, dilation τ 4 s and noise is recovered with weights within 2 % and the scale
within 1 %; the sensitivity comes out 4.0 (interval 2.2–7.4): dilation after the darker steps is not finished by their
end, so those steps read small, and the loosely determined sensitivity takes up the difference; doubling the datasheet luminance halves the fitted sensitivity exactly
and leaves the predictions unchanged.

**Real recording** (Varjo XR-4, April 2026, default display photometry): see
[open issue 36](../OPEN_ISSUES.md) for the results and what they say about sensitivity and pupil scale.

## Latency and offset

`fit.fit_calibration`, run after the light sensitivity.

### Latency from constriction onsets

When the sequence is known (always, from the app), the latency is measured rather than fitted. At every clearly
brighter step, the video change is located and the constriction onset read the standard way: the line through the
points where the pupil has made 20 % and 50 % of its constriction, extended back to the level of the second before the
change. Only constrictions of at least 0.3 mm count, and at least three are needed; the median onset is held fixed,
and its interquartile range is reported. Onsets under 0.1 s are left out and counted in a note: a reflex cannot be that
fast (the shortest reported pupil latencies are about 0.2 s), and on the Varjo calibration recordings such onsets were
constrictions that started before the display changed, probably anticipating the regular steps
([open issue 41](../OPEN_ISSUES.md)).

The onset read this way is not quite the latency: the same construction applied to the model's own constriction
lands about 0.09 τ before its start with one constriction stage (which starts at full speed) and about 0.25 τ after
it with two (which start gradually). For each candidate constriction τ the latency is therefore set to the median
onset minus that bias, so `delay` is the time to the first movement of the pupil.

Fitting the latency together with the rest does not work on real data: the fit error barely depends on it (on the
April 2026 recording, 0.145 mm at 0 s against 0.152 mm at 0.4 s), so small mismatches in the response's shape, such
as re-dilation after a constriction, which the model does not describe, drive it to 0 s. Measured onsets on the same
recording give 0.32 s (interquartile range 0.27–0.34 s over 10 steps). Without a sequence, or with fewer than three
onsets, the latency is fitted as below.

### Fitted parameters

| Parameter | Range | Fitted as |
|---|---|---|
| latency (`delay`) | 0–1.5 s | grid search, then jointly with the time constants |
| dilation τ (`attack`) | 0.3–30 s | Nelder–Mead on log τ |
| constriction τ (`release`) | 0.05–5 s | Nelder–Mead on log τ |
| transient (`transient`), optional | 0.01–3 mm | Nelder–Mead on log, with the time constants |
| escape τ (`escape`), optional | 0.3–30 s | Nelder–Mead on log τ, with the time constants |
| offset (`pupil_offset`), optional (`fit_offset`) | – | least squares, for each candidate dynamics |

For candidate dynamics, the expected pupil is computed over the window (with 30 s of signal before it so the filter
has settled), and mapped onto the measured pupil by least squares, \(PD_\text{measured} \approx c\,PD_\text{expected} + d\),
giving the scale \(k = 1/c\) and offset \(b = -d/c\). The cost is the remaining RMS, in measured millimetres. The
regression runs this way because the measurement is the noisy side: regressing the model on the measurement would pull
\(k\) towards zero whenever the pupil varies in ways the model does not (on the April 2026 recording it gave 0.40
instead of 0.62).

Without measured onsets, latency and constriction speed trade off against each other (a late fast response looks like
an early slow one), so they are fitted **jointly** rather than one after the other, from two starting points (constriction τ 0.3 s and
1 s), keeping the better. The fit uses the lightly smoothed pupil, which keeps the step edges that carry the latency.

### Guards and warnings

- A latency or time constant ending on its search limit means the model does not match the pupil yet; the notes say
  to revisit the light sensitivity fit.
- A transient below 0.1 mm (`fit.MIN_TRANSIENT`) means there is none: it is under the pupil's own fluctuation within
  a step, and the transients fitted on the Varjo calibration recordings were 0.35–1.7 mm. It is set to 0 and the other
  values are fitted again without it, since a spurious small transient also pulls the latency and time constants. A
  transient or escape τ at another limit
  usually means the participant shows little escape and the transient is only reshaping the constriction onset; the
  note suggests leaving it off.
- Pixel data (Pupil Core 2D) is refused: its scale is not defined.

### Result

The fitted parameters are the input parameters with `delay` (with `fit_offset`, also `pupil_offset` and `alignment` = `fixed`;
`pupil_correction` and by default the offset are left as they are), and with the dynamics `dynamics` = on, `attack`, `release`, `transient` and
`escape`. The app fits the transient whenever it fits the dynamics; `fit_calibration(..., fit_transient=False)` leaves
it out. The ΔPD RMS in the
window before and after is reported. Saved with the participant's parameters, they apply unchanged to the
participant's other recordings.

On synthetic recordings the fit recovers latency, time constants, transient and offset closely (see
`tests/test_alignment_and_fit.py`). On the seven Varjo calibration recordings the transient lowers the ΔPD RMS in the
sequence by 5–19 % and in the 4 s after brightening steps by 15–25 %; see [open issue 43](../OPEN_ISSUES.md).

## Glasses with a lux sensor

`photometry.fit_lux_response`. Glasses have no display photometry, and their luminance comes from the lux sensor and
the scene video (see [Luminance](luminance.md#lux-sensor-devices)), so the display fit above does not apply. What is
fitted is smaller: a **light sensitivity** \(s\) multiplying the luminance entering the model, and the pupil
**offset** \(d\), by least squares on ΔPD over the sequence,

\[
\min_{s,d} \sum_t \big( PD_\text{measured}(t) + d - PD_\text{expected}(s \cdot L(t)) \big)^2 .
\]

The luminance \(L\) is what the analysis builds with the current parameters, and the expected pupil includes the
current latency and dynamics. For each \(s\) the best offset is the mean of expected − measured, so only \(s\)
is searched: a grid over 0.001–1000, then a bounded refinement. The interval of \(s\) comes from the curvature of the
cost, with about two independent samples per second. The pupil scale is the device's (millimetres) and is not fitted:
with the luminance uncertain, scale and sensitivity cannot be told apart on one sequence ([open issue 36](../OPEN_ISSUES.md)).
Pixel data is refused, as above.

Apply sets `sensitivity`, `pupil_offset` and `alignment` = `fixed`. The RMS before is the current sensitivity with its
best offset, so the improvement shown is the sensitivity's alone; with the offset free, the sensitivity often improves
the fit little. Notes say when the expected pupil barely varies over the window (the sensor saw no change), when it
follows the measured one poorly (correlation below 0.3), when the sensitivity is at its limit or weakly determined,
and when fewer than four steps have data.

**Fixation weight (optional).** With *Also fit the fixation weight* (`fit_fixation=True`) the gaze circle's share of
the weighted colour, `fixation_weight` ([open issue 47](../OPEN_ISSUES.md)), is fitted too, within 0.05–1: eight values
first, each with its own sensitivity search, then a bounded refinement around the best. It changes the luminance
\(L = \bar L \cdot Y_w / Y_\text{frame}\), so it needs the video route and a scene where the gaze area and the
background differ (a screen in a room): a full-field calibration on a display cannot determine it. The notes say when
the cost hardly changes across the weights (below 2 %), when the weight is at a limit, and that one recording is not
enough to rely on it. Apply then also sets `fixation_weight`.

Fit on a segment where light drives the pupil, such as the calibration sequence or a rest period; a fit over a
whole task recording would absorb the workload signal it is meant to leave in ΔPD. On the 30 September 2026 Pupil Core
recording (81 s of the sequence, ten steps, laptop screen) it gives a sensitivity of 0.08 with an interval of
0.02–0.37, ΔPD RMS 0.74 → 0.72 mm and a correlation of 0.51, and says the sensitivity is weakly determined. With the
fixation weight fitted it goes to 1 (the gaze area alone), with a sensitivity of about 2, RMS 0.67 mm and a
correlation of 0.59.

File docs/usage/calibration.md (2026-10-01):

# Participant calibration

Individual differences in pupil size, light sensitivity and response speed, and the imperfectly known photometry
of a headset's display, limit how well the expected pupil matches the measured one. For the Varjo XR-4 each
participant watches a full-field **calibration sequence**, which is used in two automatic fits:

1. **Light sensitivity**: how strongly this participant's pupil responds to the display's light, and to its red,
   green and blue channels.
2. **Latency and dynamics**: response latency, dilation and constriction speed.

Both start from the **display photometry**: the headset's nominal black and white luminance and gamma, which you
provide (e.g. from the datasheet) and keep in their own file. The fits are saved in the participant's parameter
file and applied to their other recordings.

## The sequence

The default sequence is the [calibration presenter](calibration-tool.md)'s **full calibration**: the 8 grey levels of
Eckert et al. (2022), longer the darker; red, green and blue at 64, 128, 191 and 255, each after a black step; two greys
repeated; 34 steps, 291 s, in a pseudo-random order (`calibration.DEFAULT`). The presenter usually scrambles it again
for each participant, seeded by their ID: load the run file it saves (**Load sequence…**), which records the order
played, or regenerate it with `calibration.scrambled(calibration.DEFAULT, "<participant ID>")`.

The 20-step staircase used before October 2026 (greys 0 to 255, then red, green and blue at 64 to 255, 6 s each,
ascending) is still available (**Built-in** menu, `calibration.STAIRCASE_20`) for recordings made with it; its fixed
ascending order confounds luminance with time (open issues 36, 41, 43). Other sequences are loaded from a CSV:

```text
time,r,g,b,label
0,0,0,0,Black
6,36,36,36,Gray 36
...
```

Accepted layouts: a header with a time column (`time`, `t`, `timestamp`, `start`, `onset`; seconds, or
milliseconds if the header says `ms`) and `r`/`red`, `g`/`green`, `b`/`blue` columns, optionally `duration` and
`label`; or four unlabelled columns time, R, G, B. Colours may be 0–255 or 0–1. Each step lasts until the next
starts; the last uses its duration, or the median step length.

## 0. Display photometry (once per headset and settings)

In **Display photometry (datasheet)** enter the headset's black luminance (**Lmin**), white luminance (**Lmax**) and
**gamma**, then **File → Save display photometry…**. The file is remembered for that device and loaded
automatically with its recordings; load another one with **File → Load display photometry…** if the headset's
settings or firmware change.

These values do not have to be exact. The sequence cannot tell a dimmer headset from a less sensitive participant,
so any error common to all participants ends up in each participant's light sensitivity (see below). What matters
is using the same display photometry for all participants and recordings made with the same headset settings.

## 1. Locate the sequence

Open the recording and click **Find in recording**. It finds the step changes in the analysed video colour, tries
each as a start, and scores how well the sequence's colours explain the measured ones (with one gain per channel,
since recorded levels are below nominal). If the steps are evenly spaced it also tries the recording's actual
step length, so a sequence played with 10 s steps is found even though the built-in one uses 6 s. Stretches where
eye tracking was lost have no analysed colour and are left out of the score; the status bar says how much of the
sequence fell in such gaps.

The overlay turns on and the start is set. Adjust it by dragging the grey line if needed.

## 2. Fit the light sensitivity

Click **1. Fit light sensitivity** (tick *Also fit gamma* only if the datasheet gamma clearly fails). For every step
the fit takes the pupil's level at the end of the step (the mean of its last 30 %) and finds the values that make
the model match them:

| Parameter | Determined by |
|---|---|
| **Light sensitivity** | where along the grey steps the pupil stops shrinking |
| **Red/green/blue weight** | the size of the responses to the colour steps, relative to the greys |
| **Gamma** (optional) | the spacing of the grey steps |
| **Black level** (optional) | the pupil on the black steps, with the white held at its nominal value |

The pupil offset is not fitted: with the sensitivity and the display's black and white free, an offset would hide an error of them. It stays the value set by hand.
The black level needs steps long enough to dark-adapt: with short steps the black looks brighter than it is, and the fit reports the contrast it implies against the nominal one.

The result window plots the level of each step in its colour against the model before and after, with the
sensitivity's 95 % interval and warnings (e.g. when steps were still dilating at their end, or when the sensitivity
is weakly determined). **Apply** sets the values.

A sensitivity of 2 means this participant's pupil responds to the display as the standard observer would to twice
the luminance, or equally that the display is twice as bright as its photometry says. Compare sensitivities only
between participants calibrated with the same display photometry.

## 3. Fit latency and dynamics

Click **2. Fit latency and offset** (tick *Include dynamics (time constants and transient)* to fit the
dilation and constriction time constants together with the constriction beyond the steady state after brightening
steps and its re-dilation, and turn the dynamics on).
The latency is measured from the constriction onsets at the sequence's brightening steps (the result reports it with
its spread); the rest is fitted on the sequence window, and the ΔPD RMS before and after is reported. Applying it
sets:

- `delay` (latency),
- with dynamics: `dynamics` = on, `attack` and `release` (dilation and constriction time constants), `transient` and
  `escape`,

If a value ends on a search limit, a warning explains it: usually the light sensitivity fit needs another look
(sequence start, display photometry).

!!! note "The pupil scale is not fitted"
    `pupil_correction`, the multiplier on the device's pupil scale, stays the value you set (1 by default). One
    sequence does not determine it: it trades off with the light sensitivity and the black point, and a fitted value
    far from 1 was not evidence of a wrong scale ([open issue 1](../OPEN_ISSUES.md)). Set it by hand when there is a
    reason, such as a known-size reference or a device whose millimetres are known to be off. See
[Calibration fit](../processing/calibration-fit.md) for how it works.

## Glasses with a lux sensor

Pupil Core, Neon and Glasses 3 have no display photometry, so the two fits above are not available. With a lux log
(and the presenter played on the computer that recorded the tracker), **Load sequence…** takes the presenter's run
file, which places the sequence, and **Fit sensitivity and offset** fits the light sensitivity and the pupil offset
on it: see [Calibration fit](../processing/calibration-fit.md#glasses-with-a-lux-sensor). Check first that the sensor
sees the screen: a sensor dominated by room light barely follows the steps, and the fit says so.

## 4. Save

**File → Save parameters as…** and name the file after the participant. Load it with their other recordings, or
pass it to `cwtool --params` (with the display photometry file as `--display`). Participant files do not contain the display photometry, so loading one keeps the
display photometry currently in use. (Files from before this change still carry Lmin, Lmax and gamma; loading them
reproduces their original results.)

!!! warning "Light sensitivity first"
    The latency fit takes the light response as given. Running it first makes the latency and time constants absorb
    luminance errors: on the April 2026 Varjo sample, default settings gave a latency of 0 s, which is not
    physiological.

!!! tip "Adjusting by hand"
    Every fitted value stays editable. Watching the expected curve against the measured one and the **ΔPD RMS in
    sequence** while changing the sensitivity or channel weights is still a useful check of the fit.

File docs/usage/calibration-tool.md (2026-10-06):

# Calibration presenter

A self-contained web page that shows the [calibration sequence](calibration.md) to the participant, on a screen or
inside a VR headset, and logs every run. It is static (one HTML file and a small three.js build), so it works from
GitHub Pages: [open the presenter](../calibration-tool/index.html){ target=_blank }. Nothing is uploaded; sequences and
runs stay in the browser until you download them.

## Sequence editor

The sequence is a **timeline**: one block per step, coloured with the step's colour, as wide as its length.

- Drag a block to move it; drag its right edge to change its length (0.5 s steps, **Alt** for 0.1 s).
- Select a block to edit its label, RGB colour and length, or duplicate or delete it. Arrow keys select,
  **Alt**+arrows move, **+**/**−** change the length, **Ctrl/Cmd+Z** undoes.
- **Preset** loads a sequence. The default is the **full calibration** (below); the others are from Eckert et al.
  (2022): 8 gray levels, 6 s each, pseudo-random (their most robust sequence); dark-to-light and light-to-dark ramps at
  3, 6 and 10 s; blue and red ramps (shades, then tints) at 3 s; and the 20-step staircase cwtool used before October 2026. The paper describes
  its orders rather than listing them, so the pseudo-random order here is generated (fixed seed), not copied from its
  Fig. 1. The realistic *room* scene of Eckert et al. is not supported.
- **Generate…** builds gray, blue, red, green or gray + RGB primaries ramps of any length, order and duration.
- **Export CSV** / **Import CSV…** use the format of *Load sequence…* in cwtool (`time,r,g,b,label,duration`), so the
  same file drives the presenter and the analysis.

## The default: full calibration

This is also cwtool's default sequence (`calibration.DEFAULT`, in the preset order); `calibration.scrambled` gives
the order the presenter plays for a seed, with the same seeded shuffle.

One sequence for both of cwtool's fits, about 5 minutes (34 steps, 291 s), built from Eckert et al. (2022) and from what the
recordings showed (open issues 36, 40, 43):

| Part | Steps | Why |
|---|---|---|
| Gray, 8 levels (0, 36, 73, 109, 146, 182, 219, 255) | 20, 15, 10, 8, 6, 6, 6 and 12 s | Eckert et al.'s levels; the light sensitivity comes from where the pupil stops shrinking. Darker grays last longer because dilation is slow (time constants 1.6 to 9.6 s), so the end of the step is near its steady state; 255 is long to show the sustained level after the initial constriction |
| Red, green, blue at 64, 128, 191, 255 | 8 s each, every one after a linked black step of 8 s | the channel weights; the black step gives a known dark start, so the colour step is a brightening from the same state, and its end is near steady state |
| Gray 73 and 182 again | 8 s | repeats, so a reproducible model error can be told from the participant's state at that moment |

- **Order:** pseudo-random, no two consecutive levels next to each other in brightness (Eckert et al.), so luminance
  is not confounded with time (in the old ascending staircase, sensitivity could not be told from adaptation).
  Colours are mixed in with the grays. A colour and its black step are **linked** (*Keep with the previous step*):
  scrambling moves them together.
- **Irregular lengths and many changes:** 12 brightening steps from black and about as many darkening steps, of
  different sizes and lengths, give the latency (from onsets), the two time constants and the transient a range to be
  fitted on, as issue 43 asks for.
- **Adjustable:** the lengths are in the timeline. A black step after the gray 0 step just lengthens the dark.

## Running

Choose **On screen** or **In VR**, enter the **participant ID** and press start.

- **Order:** *as designed*, *scrambled, seeded by participant* (the same ID always gives the same order, so it can be
  regenerated; type a seed to override) or *scrambled with a new random seed each run*. *Keep neighbouring
  brightness levels apart* forbids two consecutive steps that are neighbours in brightness. The order for the run is
  previewed, and **Save this order as CSV** exports it.
- **Lead-in:** a neutral gray field before the first step (5 s, level 128 by default), optionally after a start
  signal (**Space**, a click, or the VR controller trigger) so the participant starts when ready.
- **On screen:** the field fills the window in full screen with the cursor hidden. **Esc** aborts.
- **In VR:** the participant is at the centre of a sphere painted in one colour (three.js, WebXR
  `immersive-vr`, no shading or tone mapping, so the field is the requested sRGB value). It needs a
  WebXR browser (a headset browser, or a desktop browser with SteamVR or Varjo Base) and an HTTPS or localhost page.
  Start the run from the desktop window; the status line follows it.

Fix the display first (constant brightness, sRGB, no night shift or HDR): the page sends sRGB values, the light
that results depends on the display.

## Run files

Each run is saved as `calibration_run_<participant>_<mode>_<date-time>.csv`, and kept in the page's list, where you
can also download all runs as one CSV. Lines starting with `#` describe the run (participant, mode, order and
seed, lead-in, start time as Unix milliseconds, frame statistics, display and browser); read them with
`pandas.read_csv(..., comment="#")`. The table has one row per step shown:

| Column | Meaning |
|---|---|
| `time`, `duration` | actual onset and length in s from the first step; the onset is the timestamp of the frame that carried the new colour, so the display adds about one frame |
| `r`, `g`, `b`, `label` | the step's colour |
| `index`, `source_index` | position played, and position in the designed sequence |
| `planned_start_s`, `planned_duration_s` | what was asked |
| `onset_unix_ms` | onset on the computer's clock, to match with recordings |
| `Y` | nominal luminance of the sRGB colour (Eckert et al. 2022, eq. 1) |
| `completed` | `false` for a step cut short by an abort |

The file loads in cwtool's *Load sequence…* as it is, giving the sequence as actually presented. Its `onset_unix_ms`
column is on the presenting computer's clock, so when that is the computer that recorded the eye tracker, cwtool
places the sequence in the recording from it without searching.

!!! note "The light in the headset is not measured yet"
    The VR session has been run in a headset, but the colour of the sphere was only checked on a normal canvas. Check
    the light in the headset with the [lux sensor](../hardware/lux-sensor.md) before relying on the nominal levels;
    see open issue 46.

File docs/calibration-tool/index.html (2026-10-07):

# Calibration Sequence Tool

Show a full-field colour sequence on a screen or in a VR headset, build and scramble your own sequences, and log every run to CSV. Made for the participant calibration of the Cognitive Workload Tool. Everything runs in this page; nothing is uploaded.

## 1. Sequence

Preset Generate… Name Import CSV… Export CSV Undo Redo

Add step Zoom

Drag a block to reorder it, drag its right edge to change its length (0.5 s steps, hold Alt for 0.1 s). With a block selected: ←→ select, Alt+←→ move, +− length, Del remove.

Label Colour R G B Length (s)

Keep with the previous step when scrambling (e.g. a dark step before a colour)

◀ Earlier Later ▶ Duplicate Delete

## 2. Run

On screen In VR (WebXR)

Participant ID Order Seed Keep neighbouring brightness levels apart

Lead-in (s) Lead-in grey Wait for a start signal (Space, click, or VR trigger) Download the CSV when the run ends Leave VR at the end

Order for this run

Save this order as CSV

Start run Abort

Before you start

- Fix the display: constant brightness (no auto-brightness, night shift or adaptive contrast), sRGB profile, HDR off. Sequence colours are sent as plain sRGB values; the actual light depends on the display.
- On screen the field fills the whole window in full screen; Esc aborts. The cursor is hidden.
- In VR the participant sits at the centre of a sphere painted in one colour, on a headset browser or a desktop browser with a WebXR runtime (SteamVR, Varjo Base, …). The page must be served over HTTPS or from localhost. Control the run from the desktop window; the participant can start it with the trigger.
- Timings are logged per frame: time is when the frame carrying the new colour was submitted; the display adds a fixed delay of about one frame.

## 3. Runs

Stored in this browser only. Download what you need.

When | Participant | Mode | Sequence | Steps | Status

Download all as one CSV Delete all runs

## Generate steps

Ramp Levels Length (s)

Darkest Lightest

Order Seed

Replace the sequence Append

Cancel Generate

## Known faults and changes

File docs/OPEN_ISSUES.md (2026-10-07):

# Open issues

Inconsistencies and suspected errors found while porting the Varjo build (`legacy-varjo`, legacy
`pupil_code/`) to the 2.0 `cwtool` package, and between the code and the Varjo manuscript
("Toward Reliable Pupillometry in Extended Reality Environments", second draft, in preparation and not yet published).
Unless stated otherwise, "the paper" below means this manuscript.

The legacy code has since been removed from `master_v2.0`; file references such as `lum_analysis.py` or `data_tools.py`
point to `legacy-varjo`.

Each issue says where it is, why it matters, what 2.0 currently does and what is proposed.
**Status** is one of: *open* (needs a decision), *kept* (2.0 reproduces the legacy behaviour until decided),
*fixed in 2.0*, *needs data* (needs a sample recording to settle).

Several of these interact. Issues 1, 2, 4, 9 and 12 in particular all change the absolute scale of the
expected or measured pupil, and the calibrated values in Table 2a (Lmax 1500–6500 cd/m²) may be absorbing
them rather than describing the headset or the participant.

Issues about the paper text only (10, 24, 25, 28, 31) were removed in September 2026, to be taken up when the paper
is revised; they remain in the git history of this file.

---

## A. Pupil model and signal

### 1. Measured pupil is multiplied by 2
- **Where:** `lum_analysis.py` (`x * (1 + pupilCoeff)`, default `pupilCoeff = 1`); 2.0 `Parameters.pupil_scale = 2.0`.
- **Problem:** the code comment says Varjo outputs a radius, but the paper says the XR-4 reports pupil
  diameter in mm. Both cannot be true. If Varjo reports a diameter, every measured pupil is doubled.
- **Related:** the Varjo validity filter keeps values between 1 and 9 mm *before* scaling, which only makes
  sense if the value is already a diameter.
- **Proposal:** check against Varjo's documentation and a sample (typical adult diameters are 2–8 mm).
  If it is a diameter, set the default to 1.0 and keep the scale as a per-participant calibration term
  (the paper already discusses glasses biasing the mm conversion).
- **Context (G. Pignoni):** Varjo confirmed by email that its output is the radius. The scaling from eye-camera
  pixels to mm also seems inconsistent between sessions, so a correction is sometimes needed; this is one reason
  for recording calibration data.
- **2.0:** each device profile declares its pupil unit and default scale (Varjo mm ×2; Pupil Core 3D mm ×1;
  pixel data has no default and is scaled by the 2021 ratio method). Participants get a `pupil_correction`
  multiplier (fitted from the calibration sequence in the next step). The 1–9 mm validity range is applied after
  scaling, and a warning is shown when the median diameter is outside 2–8 mm.
- **Varjo sample:** `left_iris_diameter_in_mm` is exactly 6.04 mm in every sample, half of a typical 11–12 mm iris,
  which supports the radius explanation. Being a constant, it cannot serve as an independent per-session scale check.
  Eye tracking runs at 200 Hz (the device profile now says so).
- **A later Varjo Base (30 September 2026 sample):** the iris column reads 12.22 mm (left) and 12.46 mm (right), twice
  the old constant, and the pupil–iris ratio (0.25) is the ratio of the columns in the new units: the file now holds
  diameters (median pupil 3.1 mm, 5–95 % 2.3–5.8). The light fit had already suggested it: its first pupil scale
  correction was 0.52, almost exactly ½. The reader now sets the scale per recording from the median iris (above 9 mm:
  scale 1; below or unreadable: scale 2), so old exports keep working. On that sample the fitted correction was
  0.54–0.72 rather than near 1, but that is not a size mismatch: on the step levels, fixing the scale at 1 fits as
  well as leaving it free (RMS 0.656 against 0.648 mm, photopic weights, black point fitted), and the free fit
  lands near 0.45 in a flat valley. The scale is not determined by one sequence (issues 36 and 42), so a fitted
  correction away from 1 says little; the diameters themselves (median 3.1 mm) are plausible.
- **Decision (September 2026):** the scale is removed from both automatic fits; `pupil_correction` stays a value set by
  hand (default 1). Physiology bounds it on that sample: the longest dark step reaches 6.4 mm and is still rising
  (asymptote 6.4–6.7 mm, recording maximum 7.7 mm), which caps the scale near 1.2, and the 2.2 mm of the white steps
  puts a floor near 0.9.
- **Status:** fixed in 2.0.

### 2. Measured pupil is shifted to match the expected mean
- **Where:** `lum_analysis.py` (`coeff = meanLux - meanRec`); 2.0 `Parameters.align_mean = True`.
- **Problem:** the mean of ΔPD is forced to about zero in every recording. This hides any constant offset,
  so absolute ΔPD levels cannot be compared between recordings, and a mis-set Lmin/Lmax or pupil scale is
  partly masked. The paper does not describe this step; its calibration procedure ("centre the expected and
  measured curves") may in practice be this automatic shift.
- **Proposal:** decide whether it is part of the method. If yes, document it in the paper and consider
  fitting the offset on the calibration sequence (per participant) instead of on each recording.
  If no, default to off.
- **Context (G. Pignoni):** no better matching method was found so far; previous publications compared recordings
  in units of ± one standard deviation of ΔPD.
- **2.0:** `alignment` chooses how the offset is found: "recording" (median over the whole recording, the 1.x
  behaviour but with the median), "baseline" (median over named events, e.g. rest periods), "fixed" (an offset
  fitted on the participant's calibration sequence and reused for their other recordings, which keeps ΔPD's
  absolute level) or "none". ΔPD is exported both in mm and in SD units.
- **Status:** fixed in 2.0.

### 3. The 0.5 s delay is applied even when dynamics are off
- **Where:** `lum_analysis.py` (delay loop sits outside `if pupilDynamics`); 2.0 `Parameters.delay = 0.5`, always applied.
- **Problem:** the paper presents the delay as the first stage of the optional dynamic correction, and gives
  200–500 ms as the physiological range. The code always delays by 500 ms.
- **Proposal:** decide whether the delay is part of the optional correction. Either way, expose it as a
  parameter (2.0 already does) and consider 0.3 s as a default within the literature range.
- **Context (G. Pignoni):** 0.5 s is a good approximation of the eye's response delay; the optional dynamics
  are known to be imperfect.
- **2.0:** the delay stays a separate parameter (default 0.5 s, always applied). The calibration fit
  (`cwtool.fit`, "Fit latency, scale and offset" in the GUI) estimates each participant's latency, dilation and
  constriction time constants, pupil scale correction and offset from the 20 steps of the sequence, given the
  operator's photometric calibration. Latency and constriction speed trade off, so they are fitted jointly.
- **Checked (September 2026):** on the seven Varjo calibration recordings the latency measured from constriction
  onsets is 0.30–0.36 s with a one-stage constriction and 0.20–0.33 s with two (issues 38, 41, 43), within the
  200–500 ms the paper cites; the fitted latency replaces the 0.5 s default per participant.
- **Status:** fixed in 2.0.

### 4. Field size used as a diameter instead of an area
- **Where:** `colour_tools.effectiveCornealFluxDensity` (`L * a * M(e)`), `fieldAngle = 160`; 2.0 `Parameters.field`.
- **Problem:** Watson & Yellott define the corneal flux density as F = L · a · M(e) with *a* the field
  **area in deg²**. The code passes 160 and the UI calls it "field angle". A 160° diameter field is
  about 20 000 deg² (π · 80²), so F is underestimated by roughly 125×. The same predicted pupil then
  needs about 125× more luminance, which may be why calibrated Lmax values sit at 1500–6500 cd/m².
  (For fields this large the formula is also outside the range it was fitted on.)
- **Proposal:** decide whether to treat the parameter as an area (and convert from the headset's FOV),
  or keep it as an empirical "field" constant and say so in the paper. Changing it will change every
  calibrated Lmax.
- **Note:** the 2021 paper (eq. 1) also describes *a* as "field diameter (degrees of view)".
- **Key point:** the formula uses luminance and field only through their product, so the two cannot be
  separated by calibration; any error in the field is absorbed into Lmax.
- **2.0:** the field is the device's visible field area in deg² (from its field of view, e.g. XR-4
  120° × 105° ≈ 9 900 deg²), and Lmin/Lmax are real luminances. Version 1 parameter files are converted exactly
  (Lmin/Lmax × 160 / area). The pilot Lmax values 1500–6500 cd/m² become about 24–105 cd/m²; the default
  Lmax is 70 cd/m² (mean pilot value, converted). A luminance-meter reading of a full-white frame on the XR-4
  would validate the approach.
- **Status:** fixed in 2.0 (needs validation with a luminance meter).

### 5. CW RMS is an RMS about the mean
- **Where:** `lum_analysis.py` (`rms` computed around `meanDistance`); 2.0 `Result.cw_rms`.
- **Problem:** the paper defines CW rms as the root-mean-square of ΔPD. The code computes it about the mean
  (a standard deviation). The two are the same only because of the mean alignment in issue 2.
- **Proposal:** define it once. If mean alignment is turned off, plain RMS of ΔPD is the more natural
  calibration error.
- **2.0:** two figures are reported: residual RMS (√mean ΔPD², the calibration error) and ΔPD SD (the unit
  for normalised ΔPD).
- **Status:** fixed in 2.0.

### 6. Pupil sampling rate is hardcoded to 100 Hz
- **Where:** `lum_analysis.py` (`sampleFreq = 100`); 2.0 `varjo.SAMPLE_RATE = 100`.
- **Problem:** filters, the delay and the ΔPD window are all defined in samples at 100 Hz. The XR-4 can
  also track at 200 Hz, and dropped samples (blinks, invalid rows) make the real rate irregular.
- **Proposal:** estimate the rate from the timestamps, and resample to a uniform grid before filtering.
- **2.0:** the measured rate is estimated from the timestamps; pupil data is resampled onto a uniform grid
  (`analysis_rate`, default 100 Hz), gaps up to `max_gap` (0.5 s) are interpolated and longer ones are left out
  of ΔPD and the RMS. Filters and windows are defined in seconds.
- **Status:** fixed in 2.0.

### 7. Attack/release filter started from 0
- **Where:** `lum_analysis.py` (`y = np.zeros_like(...)`, loop from n = 1).
- **Problem:** the filtered expected pupil starts at 0 and rises with the slow 6 s attack, producing a large
  artefact in the first seconds of every recording when dynamics are on.
- **Status:** fixed in 2.0 (filter starts at the first input value).

### 8. ΔPD windows shifted back by one window
- **Where:** `data_tools.drawDistance` (`sStart = sample * len - len`).
- **Problem:** the first two windows are identical and every window is labelled with a time one window
  (0.2 s) early.
- **Status:** fixed in 2.0 (consecutive, non-overlapping windows).

---

## B. Luminance from the video

### 9. Paper's RGB → cd/m² equation: the Lmin term is divided by the mean gain
- **Where:** paper, "Absolute luminance with per-channel panel gains"; 2.0 `luminance.absolute_luminance` (implemented as written).
- **Problem:** L_px = (L_R + L_G + L_B) / c̄ with L_C = (Lmax · c_C · C_lin + Lmin · (1 − C_lin)) · w_C.
  Dividing by c̄ also scales the black-point term, so with equal gains ≠ 1 black maps to Lmin / c̄, not Lmin.
  The paper's claim that uniform gains reduce to the plain linear mapping only holds for gains of 1.
- **Proposal:** apply the normalisation to the Lmax term only:
  L_px = Σ_C w_C · (Lmax · (c_C / c̄) · C_lin + Lmin · (1 − C_lin)).
- **Also in the code:** in the calibration fit the gains are free, so their overall scale moved the black level
  during the fit, and normalising the reported weights to a mean of 1 afterwards changed it again: the parameters
  applied were not quite those fitted.
- **2.0 (September 2026):** the proposal: gains scale the white-point term only, black is always Lmin, and scaling all
  gains changes nothing (documented in the luminance page as a change from the paper). On the synthetic participant
  the weights and scale are now recovered within 2 % and 1 % (the scale was 10 % high); the sensitivity comes out
  4.0 for a true 3, inside its interval, because dark steps read small (issue 40). On a–g (light fit, then latency,
  scale and offset with two stages and the transient), before → after:

  | | sensitivity | step-level RMS | ΔPD RMS in sequence |
  |---|---|---|---|
  | a | 50.9 → 58.4 | 0.126 → 0.112 mm | 0.132 → 0.127 mm |
  | b | 0.017 → 0.019 | 0.678 → 0.681 mm | 0.529 → 0.534 mm |
  | c | 1.57 → 1.63 | 0.175 → 0.172 mm | 0.199 → 0.199 mm |
  | d | 0.103 → 0.113 | 0.215 → 0.217 mm | 0.345 → 0.346 mm |
  | e | 10.1 → 14.7 | 0.290 → 0.256 mm | 0.264 → 0.244 mm |
  | f | 48.3 → 44.9 | 0.252 → 0.253 mm | 0.148 → 0.151 mm |
  | g | 0.050 → 0.018 | 0.307 → 0.251 mm | 0.240 → 0.220 mm |

- **Status:** fixed in 2.0; the paper's equation should be updated when the pipeline is described.

### 11. Which code produced the pilot results?
- **Where:** legacy `colour_tools.manualRGBtoLuminanceClac`, used by `readCdm2Varjo`.
- **Problem:** the legacy function is not the paper's equation. It adds `rCoeff − gCoeff/2 − bCoeff/2`
  (and so on) to the sRGB weights and then maps the result linearly between Lmin and Lmax. With the Table 2a
  gains (e.g. b_C = 20) that gives negative or extreme weights, so Table 2 was probably not computed with the
  code on `legacy-varjo`. 2.0 implements the paper's equation, with the black-point correction of issue 9.
- **Answer (G. Pignoni, September 2026):** the table came from one of several colour-weighting approaches tried on the
  Varjo branch, and that version may be lost. The paper is a draft that will be reworked to describe 2.0, so its
  pilot numbers do not need to be reproduced.
- **Status:** closed (not pursued).

### 12. Gamma 2.2 inside the piecewise sRGB curve
- **Where:** paper eq. for C_lin; legacy `relativeLuminanceClac` / `manualRGBtoLuminanceClac`; 2.0 `luminance.srgb_to_linear`.
- **Problem:** the piecewise sRGB decoding (linear below 0.04045, ((C' + 0.055) / 1.055)^γ above) is defined
  with γ = 2.4. With γ = 2.2 the two pieces do not meet: at C' = 0.04045 the linear part gives 0.00313 and the
  power part 0.00506. "2.2" is the exponent of the *pure power* approximation of sRGB (C_lin = C'^2.2).
  The legacy code also mixes 2.2 (Varjo luminance) and 2.4 (video averages).
- **Proposal:** either piecewise with 2.4 (exact sRGB) or pure power with an adjustable γ (default 2.2).
- **2.0:** switched to the pure power curve C_lin = (C'/255)^γ with γ adjustable (default 2.2). It is continuous
  for any γ and within 1 % of full scale of exact sRGB at 2.2. Compared with the previous hybrid, mid-tones decode
  about 12 % darker (code 128: 0.218 instead of 0.248), so calibrations made before this change should be
  re-checked on the sequence; this cannot be converted exactly.
- **Status:** fixed in 2.0.

### 13. Averaging gamma-encoded pixel values
- **Where:** legacy `magicwand.mean` / `meanSmall`; 2.0 `video.analyse_frame`.
- **Problem:** the mean of each area is taken on 8-bit gamma-encoded values and linearised afterwards.
  Because the decoding curve is convex, this underestimates the luminance of textured areas
  (e.g. half black, half white averages to code 128 → ~0.22 instead of 0.5 linear).
- **Proposal:** linearise per pixel, then average. This makes the video cache depend on γ, or requires caching
  linear means for a fixed decoding curve (which issue 12 would settle).
- **2.0:** pixels are linearised before averaging. Each area's per-channel histogram gives the mean of
  (C/255)^γ for a grid of γ values (1.4–3.0 in steps of 0.2), which are cached; other γ values are
  interpolated (error below 0.001 of full scale), so γ remains a live parameter without re-reading the video.
  Textured scenes now read brighter than before (a half-black, half-white area gives 0.5 instead of about 0.22).
  Older video caches are re-analysed automatically. γ is limited to 1.4–3.0.
- **Status:** fixed in 2.0.

### 14. Fixation and background weighting done on raw RGB
- **Where:** legacy `vid_analysis.subFrameAsinc` (0.65 weighting applied to encoded RGB means).
- **Problem:** the paper weights relative luminances (rL = w_fix · rL_fix + w_bg · rL_bg).
- **Status:** fixed in 2.0 (weighting on linear values, as in the paper). Results differ slightly from legacy.

### 15. Background includes the fixation area
- **Where:** legacy `magicwand` (background mask is the whole scene circle); 2.0 `VideoSettings.background_excludes_fixation = False`.
- **Problem:** the paper describes rL_bg as "the remainder of the frame". The code includes the fixation circle.
  The effect is small (the fixation circle is ~1.5 % of the scene circle) but the text and code disagree.
- **Proposal:** pick one; 2.0 supports both.
- **Reference:** Eckert et al. (2022) also define the background as "the whole screen except the fixation area".
- **2.0:** the background now excludes the gaze circle by default, matching both papers; including it remains an option.
- **Status:** fixed in 2.0.

### 16. Legacy video CSV has R and G columns swapped
- **Where:** `magicwand.mean` returns B, G, R (OpenCV order) but `subFrameAsinc` unpacks it as B, R, G;
  `readCdm2Varjo` then reads R from the "G_pixval" column and G from "R_pixval".
- **Problem:** the two swaps cancel, so luminance is correct, but `outputFromVideo.csv` is mislabelled for
  anyone reading it directly.
- **Status:** fixed in 2.0 (new cache format, RGB order).
- **Checked again (September 2026) for a green/blue swap:** none in either version. In 1.x only red and green are
  swapped, twice, which cancels; blue is never moved, and the whole-frame average weights the channels equally. In
  2.0 both decoders (PyAV, OpenCV) return pure red, green and blue H.264 frames as R, G, B
  (`tests/test_video.py::test_channels_are_in_rgb_order`); the preview converts OpenCV's BGR to RGB; the cache,
  channel gains, photopic weights and calibration sequence all use R, G, B. The April 2026 Varjo capture shows green
  at 170 s and blue at 230 s, where the built-in order (greys, red, green, blue) puts them given the located start
  and 10 s steps. The calibration scene plays the colours in R, G, B order (confirmed by the author), so the
  capture, the sequence and the analysis agree.

### 17. Fixation circle size is not defined in visual angle
- **Where:** legacy `magicwand` (radius = scene radius / 8); 2.0 `VideoSettings.fixation_ratio`.
- **Problem:** the fixation area is a fraction of the frame, so it covers a different visual angle on each
  device (Varjo, Pupil Core, Neon scene cameras have different FOVs), and the paper does not give its size.
- **Proposal:** define it in degrees per device and report the value in the paper.
- **Reference:** Eckert et al. (2022, sec. 2.6) used a fixation radius of display width / 5 (385 px, 14.8 % of the
  diagonal), 16.35° of their 110.48° diagonal field of view, with weights 26:74 (sec. 3.2.1).
  The 2.0 default is about 5° radius, roughly a tenth of their area, so the 65:35 and 26:74 weights are not directly
  comparable; the paper should report the radius next to the weights.
- **2.0:** the gaze circle is set as a radius in degrees (`fixation_radius_deg`, default 5.25° until October 2026, now
  16.35° as in Eckert et al.; 5.25° equalled the previous
  Varjo default), converted to pixels with each device's vertical field of view, assuming a linear lens mapping.
- **Status:** fixed in 2.0 (the lens mapping is approximate).

---

## C. Data ingestion

### 18. Varjo CSV columns read by position
- **Where:** legacy `readPupilVarjo` / `readGazeVarjo` / `processPupilVarjo`; 2.0 `devices/varjo.py`.
- **Problem:** columns 1, 2, 6, 24–26, 34–36, 39, 43 are hardcoded. A Varjo Base update that adds or reorders
  columns would silently read the wrong data.
- **Proposal:** read by header name once a sample export is available.
- **2.0:** columns are found by header name (checked against a Varjo Base export from April 2026, which matches the
  old positions), with the old positions as a fallback. Varjo Base on Windows writes missing values as `-nan(ind)`,
  which the reader now treats as missing (the first run on real data failed on it).
- **Status:** fixed in 2.0.

### 19. Only the left pupil was range-checked
- **Where:** `processPupilVarjo` (checks column 39 only).
- **Problem:** invalid right-eye values passed through and were averaged into "both".
- **Status:** fixed in 2.0 (each eye filtered independently).

### 20. Gaze from the left eye only
- **Where:** `vid_analysis.magicAnalysis` (`eye = "left"`); 2.0 `varjo.load(gaze_eye="left")`.
- **Problem:** the fixation area follows the left eye's projected gaze while the pupil defaults to the average
  of both eyes. Varjo also exports a combined gaze.
- **Proposal:** use the combined gaze by default; check the vertical flip and the mapping onto the
  3840 × 3744 frame (paper: "only monocular view shown" in Fig. 2) against a sample.
- **Checked on the Varjo sample:** the capture shows the left eye's view. The left eye's projection and the combined
  gaze projected to the left view coincide; the right eye's projection is offset (it is in the right view).
  2.0 now uses the combined gaze (both eyes) by default; "left" and "right" remain options.
- **Status:** fixed in 2.0.

### 21. Video frame index assumes constant frame rate
- **Where:** `readGazeVarjo` (`frame_n = int(t / (1 / fps))`); 2.0 `video.analyse_video`.
- **Problem:** if the capture is variable frame rate or starts at an offset, gaze samples drift away from the
  frames they belong to.
- **Proposal:** use the container's frame timestamps (`CAP_PROP_POS_MSEC`) and check on a sample.
- **Confirmed on the Pupil Core sample:** the scene camera's real capture times (`world_timestamps.npy`) have a
  0.23 s gap at the start and jitter, while the MP4's own timestamps are perfectly regular. A fixed 30 fps mapping
  assigned every gaze sample to the wrong frame, by up to 24 frames (0.8 s).
- **2.0:** readers can supply recorded frame timestamps; gaze samples are then matched to the nearest frame, which
  agrees with Pupil Player's `world_index` for 100 % of the sample's gaze samples. Varjo still uses the frame rate.
- **Varjo sample:** H.264 at a steady 30 fps (all frame intervals 33.33 ms), and gaze timestamps are relative to the
  first video frame, so frame-rate timing is correct for Varjo.
- **Status:** fixed in 2.0.

### 22. Event log times depend on the computer's time zone
- **Where:** `data_tools.readEvents` (dateutil parse of a naive timestamp); 2.0 `varjo.read_event_log`.
- **Problem:** a timestamp without a zone is interpreted in the local time zone of the machine running the
  analysis, so events shift by hours when analysed elsewhere. Events are also assumed to be back-to-back
  (only the first start time is read; the rest are accumulated durations).
- **Proposal:** store event times with a zone or as unix time, and read each event's own start.
- **2.0:** `tools/event_logger.py` writes times with the UTC offset and as Unix time, which the reader prefers. Each
  event starts at its own start time, so gaps between events are kept; a row without a readable start follows the
  previous event. Logs without a zone (old logger) are read in the zone of the computer that recorded when the device
  reveals it: Varjo Base names the gaze file with local time and stores UTC inside, which gives UTC+2 on the seven
  calibration recordings (CEST, April 2026). Pupil Core and Neon logs without a zone are still read in the analysing
  computer's zone.
- **Status:** fixed in 2.0 (Varjo); Pupil devices to check on a sample recording.

### 23. Lux sensor conversion constants are undocumented
- **Where:** `data_tools.readLux` (`1.706061 * x + 0.66935`, then `/ 2.2`, time × 0.001, one file per local hour).
- **Problem:** needed for Pupil Core and Neon. The origin of the constants (sensor calibration? lux → cd/m²?)
  is not documented, and hour-named files depend on the logger's local time.
- **Proposal:** document or re-derive while porting the Pupil readers (the legacy reader is on `legacy-varjo`;
  the logger that writes these files is now `tools/lux_logger.py`).
- **2.0:** ported from the 1.x Pupil Core build (`legacy-pupilCore`): average luminance = (1.706061 · lux + 0.66935) / 2.2 sr, with the three constants
  editable as "lux sensor" parameters. For a uniform field seen by a sensor with half-angle θ, E = π·L·sin²θ
  (L ≈ E / 0.79 for the 60° sensor field of view in the 2021 paper), which differs from dividing by 2.2; the origin
  of the calibration line should still be documented.
- **From the TSL2591 datasheet and the housing (September 2026):**
  - the chip's angular response (datasheet Fig. 12) is close to a cosine: over a hemisphere it integrates to 3.10,
    against π for an ideal cosine, so the bare chip is effectively an illuminance sensor and the geometry can be
    computed rather than measured;
  - the housing (`Lux Sensor/Mount Hardware/Adafruit Pupil lumiance sensor kit.stl`) has a 19 × 16.5 mm pocket for
    the Adafruit board, a 6.5 mm aperture above it, and a funnel widening to about 10.6 mm across at 7 mm from its
    base. The board sits at the bottom of the funnel (G. Pignoni), so the photodiode (0.295 mm below the top of the
    0.65 mm package, datasheet Fig. 18) is level with the funnel's base, 3.7 mm below its rim, which limits the field
    to a half-angle of 55°. For a uniform field the datasheet response integrated over that field gives E / L =
    2.12–2.15 (depending on where the chip sits under the funnel): **the 1.x constant 2.2 is right to 2–4 %**, about
    0.01 mm of modelled pupil. It is not a solid angle, as 1.x called it (the cone's solid angle is 2.70 sr), but the
    cosine-weighted field; the lux sensor page now derives it;
  - the datasheet gives responsivity only as irradiance (264 counts per µW/cm² for a 4000 K white LED, 1120–1510
    counts between units, about ±15 %); lux comes from an empirical formula (Adafruit's library in the logger);
  - effect on the model: in Watson & Yellott a luminance error of ×1.3 moves the pupil by 0.08, 0.04 and 0.02 mm at
    10, 100 and 1000 cd/m² (×2: 0.21, 0.10, 0.04 mm), so the chip's absolute spread matters little and the geometry
    more.
- **Origin of the linear calibration** (G. Pignoni's 2019 master thesis, NTNU, section 4.2, Table 2 and Figure 13): a
  projected screen in a dark room, measured by a Konica Minolta CS-2000 spectroradiometer on a 2° spot at its centre
  and by the head-mounted sensor (lux / 2.2, a field of more than 60° including the darker surround). The thesis notes
  the two diverge because of their fields of view but are linearly related, "so this measure can be used as a simple
  calibration". Regressing the spectroradiometer on the sensor gives slope 1.709 and intercept 0.54 cd/m² (r = 0.9998,
  on the rounded table), matching 1.706061 (the intercept presumably from the unrounded data). The line is thus not a
  sensor calibration but a correction of the field-of-view mismatch in that scene: it maps the sensor's field average
  onto the luminance of the scene's bright centre. It does not carry over to other scenes (in a uniform field the
  factor would be about 1), and with the video it corrects twice, since the 2021 method already turns the field
  average into the luminance at the gaze with the camera's gaze/frame ratio.
- **Proposal:** average luminance = lux / 2.2 (gain 1, offset 0), with 2.2 derived from the housing and the chip's
  lux taken as reported (±15 % between units); optionally confirm the housing's field by turning the sensor in front of
  a distant lamp in 10° steps. For Pupil devices this lowers luminance by about 1.7 relative to 1.x, about 0.1 mm of
  modelled pupil at indoor levels.
- **2.0 (September 2026):** defaults gain 1 and offset 0 (the chip's lux), with 2.2 kept and derived; the parameters
  stay editable, and parameter files that store the 1.x values keep them. To check on the Pupil sample recording.
- **Status:** fixed in 2.0 (to be checked on a Pupil recording).

---

### 26. Saved legacy settings differ from the code defaults
- **Where:** the committed `settings.pkl` (last used settings of the legacy app) vs the defaults in `analysisTool.py`.
- **Values:** scene circle `maskSize` 0.8 (default 0.5), `pupilFiltering` 60 (default 1), `pupilDynamics` on
  (default off), `cameraLum_min` 0 / `cameraLum_max` 180 (defaults 0.02 / 200), age 33.
- **Why it matters:** results depend on which set was used, and the paper should report the values.
  `pupilFiltering` 60 means a ΔPD Savitzky-Golay window of 121 windows of 0.2 s, i.e. about 24 s of smoothing,
  which limits the time resolution of ΔPD far more than the paper suggests.
- **2.0:** scene circle default changed to 0.8 (the old 0.5 covered only half of the visible Varjo disc, which the
  video preview makes obvious). The other defaults are unchanged; `cw_smoothing` is the equivalent of `pupilFiltering`.
- **2.0 (September 2026):** dynamics are on by default, with two constriction stages (the combination that behaved
  best on the calibration recordings, issue 43); the calibration fit sets the time constants per participant.
  Parameter files written before the constriction stages existed load with one stage, as they were fitted.
  `cw_smoothing` keeps its default of 1 (no extra smoothing of ΔPD beyond its 0.2 s windows).
- **Status:** fixed in 2.0.
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

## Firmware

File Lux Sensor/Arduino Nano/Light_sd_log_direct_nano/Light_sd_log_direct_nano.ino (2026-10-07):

// Lux sensor logger: reads an Adafruit TSL2591 light sensor, switching its gain to suit the light, prints each
// reading in lux on the serial port (250000 baud, one number per line: what the sensor logger and
// tools/lux_logger.py read) and appends it to an hourly CSV file on the SD card (<month>_<day>_<hour>.csv: Unix
// time in milliseconds, hour, minute, second, lux). The time comes from the board's DS1307 real-time clock (DS1307RTC).
// Hardware: Arduino Nano + Deek-Robot data logging shield + TSL2591. See ../../ReadMe.txt and docs/hardware/lux-sensor.md.
#include <Wire.h>
#include <Adafruit_Sensor.h>
#include "Adafruit_TSL2591.h"
#include <math.h>   
#include <TimeLib.h>
#include "RTClib.h"
#include <SPI.h>
#include <SD.h>

#include <DS1307RTC.h>

Adafruit_TSL2591 tsl = Adafruit_TSL2591(2591); 

bool timeSync = false;
int  syncSecond= 61;
int  syncSecondPrev= 61;
uint64_t syncMillis = 0ULL;
long syncMillisStamp = 0;  
int frequency= 35;
const int ledPin =  LED_BUILTIN;// the number of the LED pin
int ledState = LOW;             // ledState used to set the LED
const long ledInterval = 1000;           // interval at which to blink (milliseconds)
long previousLedMillis = 0;
float frameIntervalMillis = 1.0/frequency;  
long prevFrameMillis = 0;  
long frameCount = 1;

File myFile;
const int chipSelect = 10;



float advancedRead(void)
{
  // More advanced data read example. Read 32 bits with top 16 bits IR, bottom 16 bits full spectrum
  // That way you can do whatever math and comparisons you want!
  uint32_t lum = tsl.getFullLuminosity();
  uint16_t ir, full;
  ir = lum >> 16;
  full = lum & 0xFFFF;
  return(tsl.calculateLux(full, ir));
}





void configureSensor(void){
  tsl.setGain(TSL2591_GAIN_LOW);    // 1x gain (bright light)
  //tsl.setGain(TSL2591_GAIN_MED);      // 25x gain
  //tsl.setGain(TSL2591_GAIN_HIGH);   // 428x gain
  //tsl.setGain(TSL2591_GAIN_MAX);   // 9876x gain
  
  // Changing the integration time gives you a longer time over which to sense light
  // longer timelines are slower, but are good in very low light situtations!
  tsl.setTiming(TSL2591_INTEGRATIONTIME_100MS);  // shortest integration time (bright light)
  // tsl.setTiming(TSL2591_INTEGRATIONTIME_200MS);
  //tsl.setTiming(TSL2591_INTEGRATIONTIME_300MS);
  // tsl.setTiming(TSL2591_INTEGRATIONTIME_400MS);
  // tsl.setTiming(TSL2591_INTEGRATIONTIME_500MS);
  // tsl.setTiming(TSL2591_INTEGRATIONTIME_600MS);  // longest integration time (dim light)

  /* Display the gain and integration time for reference sake */  
  Serial.println(F("------------------------------------"));
  Serial.print  (F("Gain:         "));
  
  tsl2591Gain_t gain = tsl.getGain();
  switch(gain){
  case TSL2591_GAIN_LOW:
    Serial.println(F("1x (Low)"));
    break;
  case TSL2591_GAIN_MED:
    Serial.println(F("25x (Medium)"));
    break;
  case TSL2591_GAIN_HIGH:
    Serial.println(F("428x (High)"));
    break;
  case TSL2591_GAIN_MAX:
    Serial.println(F("9876x (Max)"));
    break;
  }
  Serial.print  (F("Timing:       "));
  Serial.print((tsl.getTiming() + 1) * 100, DEC); 
  Serial.println(F(" ms"));
  Serial.println(F("------------------------------------"));
  Serial.println(F(""));
}

void setup(void){
  Serial.begin(250000);
  //while (!Serial) { delay(1);}
  pinMode(ledPin, OUTPUT);

  if (tsl.begin()) { Serial.println(F("Found a TSL2591 sensor"));}
  else { Serial.println(F("No sensor found ... check your wiring?"));}



  Serial.print("Initializing SD card...");
  // On the Ethernet Shield, CS is pin 4. It's set as an output by default.
  // Note that even if it's not used as the CS pin, the hardware SS pin 
  // (10 on most Arduino boards, 53 on the Mega) must be left as an output 
  // or the SD library functions will not work. 
  pinMode(SS, OUTPUT);
   
  if (!SD.begin(chipSelect)) {
    Serial.println("initialization failed!");
    return;
  }
  Serial.println("initialization done.");

  configureSensor();
  syncTime();
}

float unifiedSensorAPIRead(void){
  /* Get a new sensor event */ 
  float mLux=advancedRead();

  
  /* Display the results (light is measured in lux) */
  //Serial.print(F("[ ")); Serial.print(event.timestamp); Serial.print(F(" ms ] "));

  if (isnan(mLux)){
    /* Light is too low for the current gain */
  
    tsl2591Gain_t gain = tsl.getGain();
    switch(gain){
      case TSL2591_GAIN_LOW:
        tsl.setGain(TSL2591_GAIN_MED);
        mLux=advancedRead();
        break;
      case TSL2591_GAIN_MED:
        tsl.setGain(TSL2591_GAIN_HIGH);
        mLux=advancedRead();
        break;
      case TSL2591_GAIN_HIGH:
        tsl.setGain(TSL2591_GAIN_MAX);
        mLux=advancedRead();
        break;
      case TSL2591_GAIN_MAX:
        mLux=0;
        break;
      }
  }

  if (mLux <= 0) {
    /* Light is too hight for the current gain */
    tsl2591Gain_t gain = tsl.getGain();
    switch(gain){
      case TSL2591_GAIN_LOW:
        mLux=100000;
        break;
      case TSL2591_GAIN_MED:
        tsl.setGain(TSL2591_GAIN_LOW);
        mLux=advancedRead();
        break;
      case TSL2591_GAIN_HIGH:
        tsl.setGain(TSL2591_GAIN_MED);
        mLux=advancedRead();
        break;
      case TSL2591_GAIN_MAX:
        tsl.setGain(TSL2591_GAIN_HIGH);
        mLux=advancedRead();
        break;
    }
  }


  Serial.println(mLux);
    tsl2591Gain_t gain = tsl.getGain();
    switch(gain){
      
    case TSL2591_GAIN_LOW:
      if(mLux<6000){
        tsl.setGain(TSL2591_GAIN_MED);}
      break;

    case TSL2591_GAIN_MED:
      break;

    case TSL2591_GAIN_HIGH:
      break;

    case TSL2591_GAIN_MAX:
      break;
    }


  return (mLux);

}

void syncTime() {
  tmElements_t tm;
  if (RTC.read(tm)) {
    syncSecond=int(tm.Second);
    syncSecondPrev = syncSecond;
 

  Serial.println("syncTime()");
  
   
  
  
  while(!timeSync){ 
    tmElements_t tm;
    RTC.read(tm);
    syncSecond= int(tm.Second); 
    if(syncSecondPrev!=syncSecond){

      setTime(tm.Hour,tm.Minute,tm.Second,tm.Day,tm.Month,tmYearToCalendar(tm.Year));
      syncMillis =now()*1000ULL;
      syncMillisStamp =  millis();
      prevFrameMillis = syncMillisStamp;
    
      timeSync=true;
        Serial.println("Time synced!");
     print2digits(tm.Hour);
    Serial.write(':');
    print2digits(tm.Minute);
    Serial.write(':');
    print2digits(tm.Second);
    Serial.print(", Date (D/M/Y) = ");
    Serial.print(tm.Day);
    Serial.write('/');
    Serial.print(tm.Month);
    Serial.write('/');
    Serial.print(tmYearToCalendar(tm.Year));
    Serial.println();
      }
    syncSecondPrev = syncSecond; 
  }}
}


void loop(void){ 
unsigned long currentMillis = millis();
  
    if (currentMillis - previousLedMillis >= ledInterval) {
    // save the last time you blinked the LED
    previousLedMillis = currentMillis;

    // if the LED is off turn it on and vice-versa:
    if (ledState == LOW) {
      ledState = HIGH;
    } else {
      ledState = LOW;
    }

    // set the LED with the ledState of the variable:
    digitalWrite(ledPin, ledState);
  }

  
  float luxValue = unifiedSensorAPIRead();





    if((currentMillis - prevFrameMillis)/1000.00 >= frameIntervalMillis) {

      //Serial.print("sUtime = ");
      //Serial.println (now());
      //Serial.print("mUtime = ");
      uint64_t millsUtime= currentMillis - syncMillisStamp + syncMillis;   
      uint64_t xx = millsUtime/1000000000ULL;
       //if (xx >0) Serial.print((long)xx);
       //Serial.print((long)(millsUtime - xx*1000000000));
       //Serial.println ();
      
      //Serial.print("Frame = ");
      //Serial.print(frameCount);
      //Serial.write('-');
      //Serial.println(frameCount/((currentMillis - syncMillisStamp)/1000));
      //DateTime rtcTime = rtc.now();
       //Serial.print("Time = ");
       //Serial.print(hour());
       //Serial.write(':');
       //Serial.print(minute());
      //Serial.print(rtcTime.minute());
            
       //Serial.write(':');
       //Serial.println(second());
      //Serial.print(rtcTime.second());
      //Serial.println();



      prevFrameMillis=currentMillis;


      String fileName = String(month()) +"_"+ String(day()) +"_"+ String(hour()) + ".csv";
      //Serial.println(fileName);
      myFile = SD.open(fileName , FILE_WRITE);
        
        
      if (myFile) {

        if (xx >0) myFile.print((long)xx);
        myFile.print((long)(millsUtime - xx*1000000000));
        myFile.write(',');
        myFile.print(hour());
        myFile.write(',');
        myFile.print(minute());
        myFile.write(',');
        myFile.print(second());
        myFile.write(',');
        myFile.println(luxValue);
        

        myFile.close();

         

         
        }  else {
        // if the file didn't open, print an error:
        //Serial.println("error opening test.csv");
        }
        
        frameCount = frameCount+1;
      
     }



  

}

void print2digits(int number) {
  if (number >= 0 && number < 10) {
    Serial.write('0');
  }
  Serial.print(number);
}

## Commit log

2019-05-12 adding the lux logghing feature
    [Adafruit Pupil lumiance sensor kit.stl]
2019-05-13 no more time correction for the arduino saved lux
2020-02-01 Moteino support as lux sensor receiver
2020-03-10 filtering on video luminance and auto measurement of frame size
2022-04-13 adjusting filtering for tobii g3
2026-01-22 good stage of support for varjo
2026-04-20 Add user-configurable colour coefficients, gamma, and field angle
    Exposes RGB channel weights, display gamma, and HMD field angle as
    editable parameters in the UI so users can calibrate for display
    variability and perceptual differences without touching source code.
    - settingsDict: add cameraRCoeff (0.4), cameraGCoeff (0.0),
    cameraBCoeff (0.2), cameraGamma (2.2), fieldAngle (160) with
    defaults matching previous hardcoded values
    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
